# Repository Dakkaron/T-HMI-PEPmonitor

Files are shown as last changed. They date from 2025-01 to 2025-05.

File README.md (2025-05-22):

# PEPit Physiotherapy Game Console

(Für den Text in Deutsch bitte nach unten scrollen.)

## Disclaimer

PEPit is a toy. It uses a cheap commodity airpressure sensor to control games, which can help kids enjoy their physiotherapy more. It is not a medical product, it doesn't have research, papers or a big pharma company behind it. It does not give medical or physiotherapy advice and in no way does it replace an actual physician or physiotherapist. If you use PEPit you are aware that it is only a toy and not a medical product. If you use it you do so at your own risk and I will not be held liable for anything you do with your PEPit. You have been warned.

## Overview

Physiotherapy is challenging, especially for children with chronic conditions like Cystic Fibrosis. It takes time, is repetitive and often feels like a constant fight to get the child to actually do it right.

PepIt is a small handheld games console that connects to compatible physiotherapy devices (see list below). It automatically monitors the execution of physiotherapy tasks and rewards the player in game when the tasks are executed correctly.

It can also record every time it's used, so that your doctor or physiotherapist can review the data later.

This targets ages 5-10 due to the simplicity of the games so far, though anyone can use it.

PepIt is currently in early access, more games and features will follow.

## Compatible physiotherapy devices

- **Pari PEP S** with [Manometer Adapter](https://www.pari.com/int/products/pari-pep-systems/) (or similar devices)
- **Cegla RC-Cornet** and **RC-Cornet Plus** with [Pressure Measurement Adapter](https://cegla.de/files/downloads/manuals/RC-Druck-Mess-Adapter-manual-de.pdf)
- **Pari Boy** with **[LC Sprint Nebuliser](https://www.pari.com/int/products/inhalation-devices-for-the-lungs/pari-boy-classic-int/)**, using the Pari PEP S Manometer Adapter
- **[Pari E-Flow rapid](https://www.pari.com/int/products/inhalation-devices-for-the-lungs/eflow-rapid-nebuliser-system/)**, using the Pari PEP S Manometer Adapter
- Other inhalers or PEP devices that can fit the Pari PEP S or RC-Cornet manometer adapters
- Other inhalers or PEP devices that have manometer adapters
- Trampolines, using the Trampoline Sensor Addon (coming soon)

## Key Features

- **Make therapy fun**: Games with long-term motivation make the therapy engaging.
- **Reduce trouble**: No need to tell your kid that the task should be done better. PepIt automatically takes care of this.
- **Super easy to use**: PepIt is a standalone device. No booting a PC, trouble with glitchy Bluetooth connections or anything. Simply turn it on and use it.
- **Log therapy executions**: PepIt can optionally log all physiotherapy sessions so that your physiotherapists or doctors can review them later.
- **Configurable therapy routines**: Easily adjust PepIt to follow exactly the therapy routine your physiotherapist or doctor prescribed.
- **LUA-based, extendable game system**: Download additional games to the SD card later on. Or even create your own!

# PepIt Physiotherapie-Spielekonsole (Deutsch)

## Disclaimer

PEPit ist ein Spielzeug. Es verwendet billige, leicht verfügbare Luftdrucksensoren um Spiele zu steuern. Das kann dabei helfen, dass Kinder mehr Spaß an ihrer Physiotherapie haben. PEPit ist kein Medizinprodukt. Es hat weder Forschung, wissenschaftliche Arbeit oder einen Pharma-Konzern hinter sich. Es gibt keine Ratschläge im Bezug auf Medizin oder Physiotherapie und ersetzt auf keine Weise einen Arzt oder Physiotherapeuten. Wenn Sie PEPit verwenden, dann sind Sie sich hiermit bewusst, dass es ein Spielzeug und kein Medizinprodukt ist. Sie verwenden PEPit auf eigene Gefahr und eigenes Risiko hin und ich übernehme keine Haftung für was auch immer sie damit tun.

## Überblick

Seien wir mal ehrlich, Physiotherapie ist anstrengend, insbesondere für Kinder mit chronischen Krankheiten wie Zystische Fibrose/Mukoviszidose. Die Therapie frisst Zeit, ist monoton und es ist ein dauerhafter Kampf, das Kind dazu zu bringen, sie richtig auszuführen.

PepIt ist eine kleine tragbare Spielkonsole, die man mit kompatiblen Physiotherapiegeräten (siehe nachfolgende Liste) verbinden kann. Es erkennt automatisch die Ausführung der Physiotherapie und belohnt die Spielerin/den Spieler, wenn die Therapie korrekt ausgeführt wurde.

Optional können Nutzungsstatistiken von PepIt automatisch auf der SD-Karte gespeichert werden, sodass das medizinische Personal die Häufigkeit und Qualität der Therapieausführungen später auswerten kann.

PepIt zielt auf Kinder im Alter von 5 bis 10 Jahren ab, kann allerdings von Leuten aller Altersgruppen verwendet werden.

Aktuell befindet sich PepIt noch im Early Access. Weitere Spiele und Features werden im Laufe der Zeit folgen.

## Kompatible Physiotherapiegeräte

- **Pari PEP S** mit dem [Druckanzeiger-Adapter](https://www.pari.com/de/produkte/pari-pep-systeme/) (oder ähnliche Geräte)
- **Cegla RC-Cornet** und **RC-Cornet Plus** mit [Druck-Mess-Adapter](https://cegla.de/files/downloads/manuals/RC-Druck-Mess-Adapter-manual-de.pdf)
- **Pari Boy** mit **[LC Sprint Nebuliser](https://www.pari.com/int/products/inhalation-devices-for-the-lungs/pari-boy-classic-int/)**, unter Verwendung des Pari PEP S Druckanzeiger-Adapters
- **[Pari E-Flow rapid](https://www.pari.com/int/products/inhalation-devices-for-the-lungs/eflow-rapid-nebuliser-system/)**, unter Verwendung des Pari PEP S Druckanzeiger-Adapters
- Andere Inhalations- oder PEP-Geräte, auf die mit dem Pari PEP S Druckanzeiger-Adapter oder dem RC-Cornet-Druck-Mess-Adapter kompatibel sind
- Andere Inhalations- oder PEP-Geräte mit Manometeranschluss oder Druckmess-Adapter
- Trampoline unter Verwendung des Trampolin-Sensor-Addons (kommt demnächst)

## Wichtigste Features

- **Interessantere Therapie**: Spiele mit Langzeitmotivation machen die Therapie interessanter.
- **Weniger Ärger**: Mit PepIt müssen Sie nicht mehr mit dem Kind darüber streiten, ob es die Therapie korrekt ausführt. PepIt übernimmt das automatisch.
- **Sehr einfach zu verwenden**: PepIt ist Standalone. Man braucht dafür keinen PC booten, kein Handy per Bluetooth koppeln oder sonst etwas. Einfach einschalten und es nutzen.
- **Therapie loggen**: Optional kann PepIt die Nutzung auf die SD-Karte loggen, sodass das zuständige medizinische Personal sie im Nachhinein auswerten kann.
- **Anpassbare Therapiepläne**: Die Therapiepläne können in PepIt leicht auf die Anordnung der Physiotherapeuten oder Ärzte angepasst werden.
- **LUA-basiertes, erweitertes Spielsystem**: Zusätzliche Spiele können nachträglich auf die SD-Karte gespielt werden. Es ist sogar möglich, selbst welche zu erstellen!

## Bauanleitung
[Hier klicken um zur Bauanleitung zu kommen.](docs/Parts_de.md)

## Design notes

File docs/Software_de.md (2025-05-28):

# SD-Karte vorbereiten

1. Die SD-Karte mit einem Computer verbinden. Dafür kann entweder ein integrierter SD-Karten-Slot im PC oder ein SD-Karten-Adapter verwendet werden.
2. Die Datei sdcardcontent.zip vom neuesten [Release](https://github.com/Dakkaron/T-HMI-PEPmonitor/releases) herunterladen und den Inhalt auf die SD-Karte entpacken.

# Firmware auf LILLYGO T-HMI aufspielen

1. Das neueste firmware.bin von der [Release-Seite](https://github.com/Dakkaron/T-HMI-PEPmonitor/releases) herunterladen.
1. LILLYGO T-HMI per USB-Kabel mit dem PC verbinden. Sollte das Display des LILLYGO T-HMI nicht angehen, sobald es mit dem PC verbunden ist, bitte ein USB-A-auf-USB-C-Kabel verwenden. Bei der Verwendung von USB-C-auf-USB-C-Kabeln kann es zu Problemen kommen.
2. [flash_download_tool](https://dl.espressif.com/public/flash_download_tool.zip) herunterladen und ausführen.
3. Im flash_download_tool `ChipType:` auf `ESP32-S3` stellen:
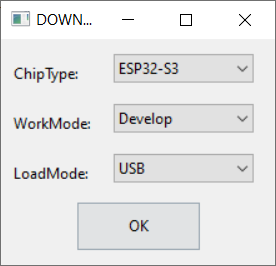
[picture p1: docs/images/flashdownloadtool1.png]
flash_download_tool
 und mit `OK` bestätigen.
4. Auf der zweiten Seite folgende Einstellungen auswählen:
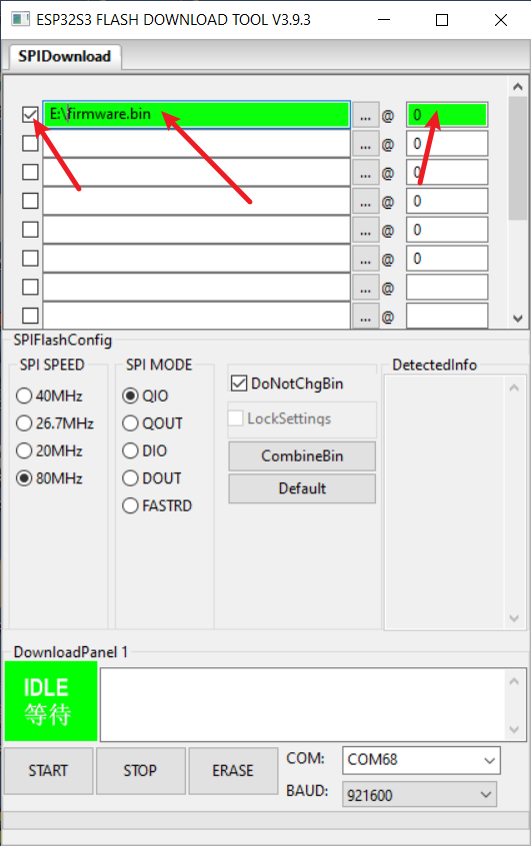
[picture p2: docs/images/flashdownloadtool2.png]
flash_download_tool

   * Oberste Checkbox am linken Rand aktivieren
   * Im Textfeld rechts neben der Checkbox den Pfad zu `firmware.bin` angeben
   * Sicherstellen, dass im rechtesten Textfeld der Zeile eine 0 ist.
   * Rechts unten bei `BAUD:` 921600 eingeben.
   * Bestätigen mit einem Click auf `START`
5. Wenn das Hochladen abgeschlossen ist, kann der T-HMI vom PC getrennt werden.

# Testen

1. MicroSD-Karte in den Slot im T-HMI einschieben.
2. Das T-HMI per USB mit dem PC verbinden.
3. Das T-HMI sollte beim ersten Start die Touchscreen-Kalibrierung anzeigen, danach wird das Hauptmenü angezeigt.

Nächster Schritt: [Zusammenbau](Assembly_de.md)

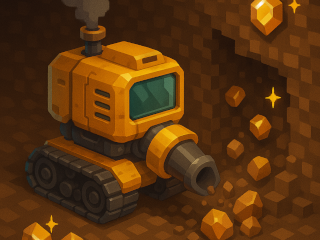
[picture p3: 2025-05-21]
SDCardContent/games/miner/gfx/win/win1.bmp

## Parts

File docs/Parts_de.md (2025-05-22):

# Benötigte Werkzeuge

- Schraubenzieher
- Lötkolben mit Lötzinn
- Werkzeug zum Abisolieren von Kabeln
- 3D-Drucker (optional)
- PC mit Windows (Andere Betriebssysteme sind möglich, werden aber in diesem Guide aktuell nicht behandelt)
- SD-Karte zu USB Adapter (falls man im PC keinen SD-Karten-Slot hat)
- Patafix oder doppelseitiges Klebeband

# Benötigte Bauteile

## Elektronische Bauteile

- LILLYGO T-HMI: https://lilygo.cc/products/t-hmi
- Luftdrucksensor: https://de.aliexpress.com/item/1005006421627550.html

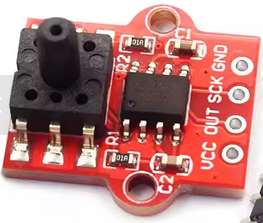
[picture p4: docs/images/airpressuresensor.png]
Luftdrucksensor

- 1S Akku mit PH2.0 Anschluss, mindestens 200mA (https://de.aliexpress.com/item/1005007256417369.html)
- MicroSD-Karte mit mindestens 1GB und maximal 32GB.

## Schrauben

- 4x M3x25 Schrauben
- 4x M3 Muttern, viereckig
- 4x M2x10 Schrauben

## Sonstiges

- Doppelseitiges Klebeband, am Besten Tesa Powerstrips Small

## 3D-Druck

- Obere Hälfte: (https://github.com/Dakkaron/T-HMI-PEPmonitor/blob/main/3DPrint/T_HMI_PEP_case_v3.2_top.stl)
- Untere Hälfte: (https://github.com/Dakkaron/T-HMI-PEPmonitor/blob/main/3DPrint/T_HMI_PEP_case_v3.2_bottom_with_tpu.stl)
- Schlauch-Adapter: (https://github.com/Dakkaron/T-HMI-PEPmonitor/blob/main/3DPrint/PEP_adapter.stl)

Der Schlauchadapter muss mit flexiblem Material (z.B. TPU- oder TPE-Filament) gedruckt werden.

Sollte kein 3D-Drucker zur Verfügung stehen, bietet sich der Druckservice von [JLC3DP](https://jlc3dp.com) an.

### Anleitung für JLC3DP

1. LadenSie die drei STL Dateien aus dem letzten Punkt herunter.
2. Öffnen sie [https://jlc3dp.com](https://jlc3dp.com) in ihrem Browser.
3. Klicken sie auf "Order Now"
4. Klicken sie auf "Add 3D Files" und fügen sie alle drei STL-Dateien nacheinander hinzu.
5. Für die beiden Gehäuseteile wählen sie einen passenden Druckprozess und Material aus. `FDM(Plastic)` -> `PLA` funktioniert gut, aber andere Materialien sollten auch verwendbar sein.
6. Für den PEP_adapter.stl wählen sie `FDM(Plastic)` -> `TPU`
7. Farben können beliebig gewählt werden.
8. Drücken Sie "Save to cart" und folgen Sie dem Bestellprozess.
9. `Global Direct Line`-Versand ist mit Abstand der Billigste, dauert dafür normal 1-2 Wochen.

Nächster Schritt: [Software installieren](Software_de.md)

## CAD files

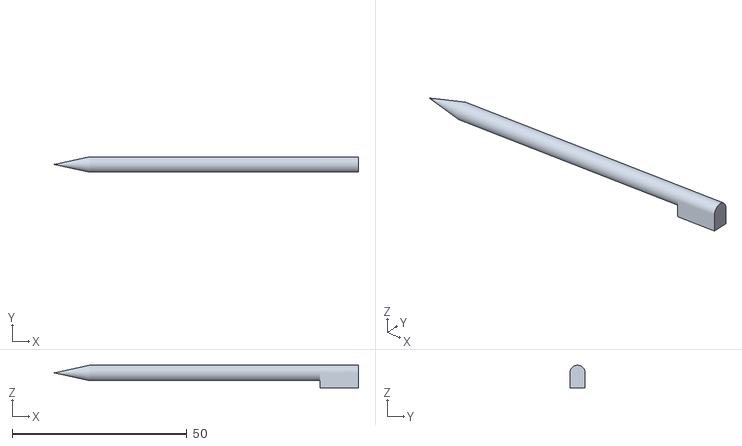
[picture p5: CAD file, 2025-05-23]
3DPrint/Stylus.stl
87.0 x 4.42 x 6.47

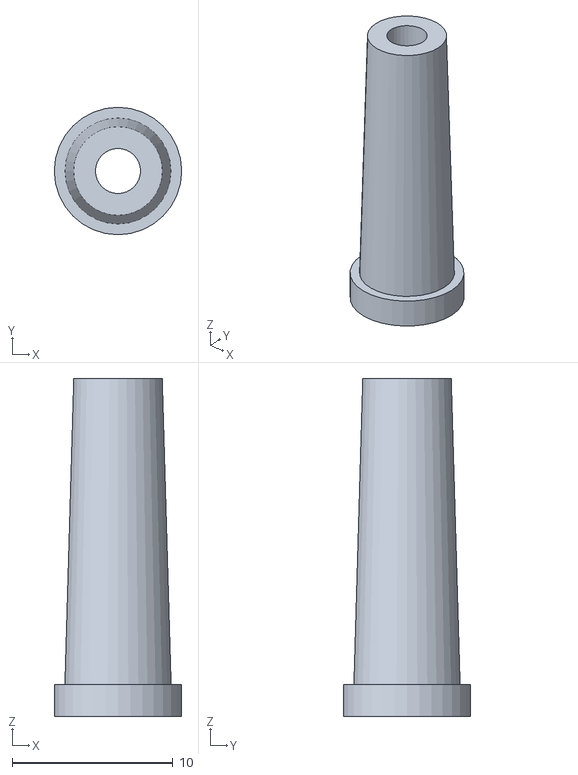
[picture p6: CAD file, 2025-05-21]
3DPrint/PEP_adapter.stl
7.92 x 7.92 x 21.0

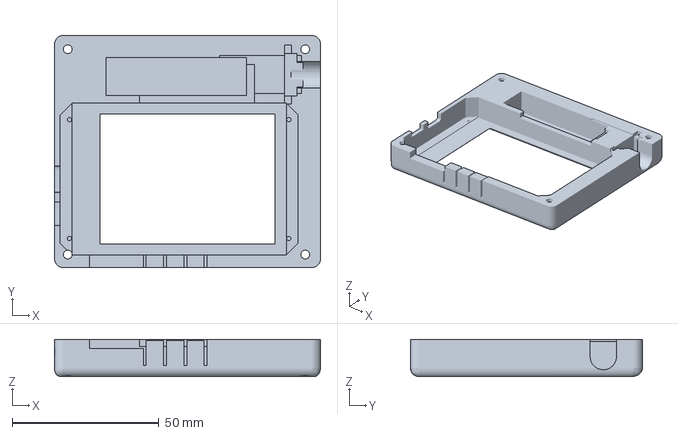
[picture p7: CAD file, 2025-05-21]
3DPrint/T_HMI_PEP_case_v3.3_top_with_logo.3mf
90.7 x 79.2 x 12.8 mm

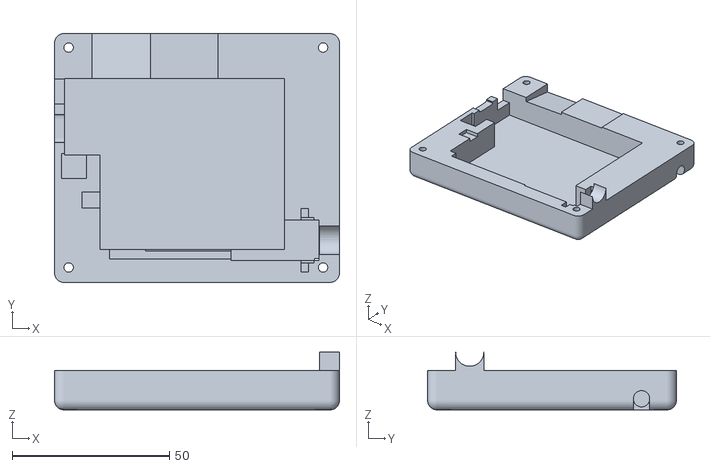
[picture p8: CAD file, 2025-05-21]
3DPrint/T_HMI_PEP_case_v3.3_bottom.stl
90.7 x 79.2 x 18.4

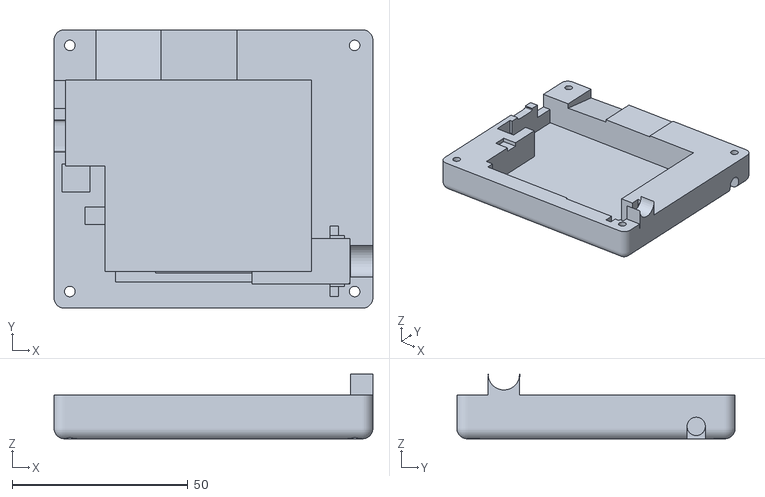
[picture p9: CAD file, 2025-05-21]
3DPrint/T_HMI_PEP_case_v3.3_bottom_hexnuts.stl
90.7 x 79.2 x 18.4

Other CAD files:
3DPrint/T_HMI_PEP_case_v3.3_top.stl

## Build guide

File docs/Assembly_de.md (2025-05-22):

# Löten

- Das bei dem T-HMI mitgelieferte Grove-Kabel (das Kabel mit den vier Adern) in der Mitte durchschneiden und die Adern rund 5mm tief abisolieren.
- Die vier Adern in der folgenden Reihenfolge an den Luftdrucksensor anlöten:
   - Schwarz -> GND
   - Rot -> VCC
   - Gelb -> OUT
   - Weiß -> SCK

# Verkablen

- Den Grove-Connector vom letzten Schritt in den mittleren Grove-Steckplatz am T-HMI anschließen.
- Den Akku an den `BAT`-Steckplatz am T-HMI anschließen

# Verschrauben

- Das T-HMI in den oberen Teil des Gehäuses einsetzen und mit den vier M2x10-Schrauben verschrauben.
- Die vier Muttern in die Aussparungen des unteren Gehäuses eindrücken.
- Die Batterie mittels Patafix oder doppelseitigem Klebeband (z.B. Tesa Power Strips Small) in die untere Gehäusehälfte kleben.
- Den Luftdrucksensor in die passende Aussparung in der oberen Gehäusehälfte einsetzen.
- Die obere Gehäusehälfte auf die Untere aufsetzen.
- Die vier M3-Schrauben in die Ecken der oberen Gehäusehälfte einsetzen und festschrauben.

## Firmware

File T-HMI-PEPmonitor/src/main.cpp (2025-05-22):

#include <Arduino.h>
#define CONFIG_SPIRAM_SUPPORT 1

#include "systemconfig.h"
#include "constants.h"

#include <SD_MMC.h>
#include <FS.h>
#include <SPI.h>
#include <SD.h>
#include <OneButton.h>

#include "hardware/gfxHandler.hpp"
#include "hardware/pressuresensor.h"
#include "hardware/touchHandler.h"
#include "hardware/wifiHandler.h"
#include "hardware/sdHandler.h"
#include "games/games.h"
#include "hardware/serialHandler.h"
#include "hardware/powerHandler.h"
#include "physioProtocolHandler.h"
#include "updateHandler.h"

void setBrightness(uint8_t value) {
  static uint8_t _brightness = 0;

  if (_brightness == value) {
    return;
  }
  value = _min(16, value);
  if (value == 0) {
    digitalWrite(BK_LIGHT_PIN, 0);
    delay(3);
    _brightness = 0;
    return;
  }
  if (_brightness == 0) {
    digitalWrite(BK_LIGHT_PIN, 1);
    _brightness = SCREEN_BRIGHTNESS_STEPS;
    delayMicroseconds(30);
  }
  int from = SCREEN_BRIGHTNESS_STEPS - _brightness;
  int to = SCREEN_BRIGHTNESS_STEPS - value;
  int num = (SCREEN_BRIGHTNESS_STEPS + to - from) % SCREEN_BRIGHTNESS_STEPS;
  for (int i = 0; i < num; i++) {
    digitalWrite(BK_LIGHT_PIN, 0);
    digitalWrite(BK_LIGHT_PIN, 1);
  }
  _brightness = value;
}

void setup() {
  pinMode(PWR_ON_PIN, OUTPUT);
  digitalWrite(PWR_ON_PIN, HIGH);
  pinMode(BK_LIGHT_PIN, OUTPUT);
  digitalWrite(BK_LIGHT_PIN, HIGH);

  esp_log_level_set("gpio", ESP_LOG_ERROR);

  Serial.setRxBufferSize(10240);
  Serial.setTxBufferSize(1024);
  Serial.begin(115200);

  pinMode(PWR_EN_PIN, OUTPUT);
  digitalWrite(PWR_EN_PIN, HIGH);

  tft.init();
  tft.setRotation(SCREEN_ROTATION);
  tft.setSwapBytes(true);
  tft.fillScreen(TFT_BLACK);

  setBrightness(16);

  initGfxHandler();
  tft.setTextSize(2);
  tft.drawString("Nicht", 10, 10);
  tft.drawString("blasen!", 10, 25);
  initPressureSensor();

  initTouch();

  buttonPwr.attachClick(power_off);
  buttonPwr.attachLongPressStop(power_off);
  buttonUsr.attachLongPressStop(runTouchCalibration);

  randomSeed(analogRead(0));
  
  String errorMessage;
  initSD(&errorMessage);
  checkFailWithMessage(errorMessage);
  checkForPrefsReset();
  initSystemConfig(&errorMessage);
  checkFailWithMessage(errorMessage);

  drawBmp("/gfx/splash.bmp", 0, 0);
  uint8_t defaultTextDatum = tft.getTextDatum();
  tft.setTextColor(TFT_BLACK);
  tft.setTextDatum(TR_DATUM);
  tft.drawString("Version "+String(VERSION), 320, 2);
  tft.setTextDatum(defaultTextDatum);
  delay(1000);
  Serial.print("PEPit Version '");
  Serial.print(VERSION);
  Serial.println("'");
  Serial.print("Initializing peripherals....");
  delay(1000);

  Serial.println(F("done"));
  
  Serial.print("PEPit Version '");
  Serial.print(VERSION);
  Serial.println("' initialized");

  tft.setTextSize(1);
  tft.drawString("Warte auf WLAN-Verbindung...", 0, 230);

  uint32_t requiredTaskTypes = runProfileSelection();
  runGameSelection(requiredTaskTypes);
  displayPhysioRotateScreen();
}

void loop() {
  buttonPwr.tick();
  buttonUsr.tick();
  handleSerial();
  handlePhysioTask();
  /*Serial.print("Free heap: ");
  Serial.println(ESP.getFreeHeap());*/
}

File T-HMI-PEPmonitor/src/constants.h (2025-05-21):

#ifndef __CONSTANTS_H__
#define __CONSTANTS_H__
#include <Arduino.h>

#define VERSION "1.1"

#define LAST_BLOW_SUCCEEDED 0B00000001
#define LAST_BLOW_FAILED    0B00000010
#define NEW_BLOW            0B00000100

#define PRESSURE_BAR_WIDTH 180
#define PRESSURE_BAR_HEIGHT 10
#define PRESSURE_BAR_X 1
#define PRESSURE_BAR_Y 190

#define PRESSURE_SENSOR_DIVISOR 65L
#define PRESSURE_SENSOR_CUTOFF_LIMIT 500
#define PRESSURE_SENSOR_SMOOTHING_NUM_READINGS 10
#define PRESSURE_SENSOR_MAX_SKIPS 10;

#define PRESSURE_SENSOR_CUMULATIVE_ERROR_FACTOR 16

#define SCREEN_BRIGHTNESS_STEPS 16
#define SCREEN_ROTATION 3
#define SCREEN_WIDTH 320
#define SCREEN_HEIGHT 240

#define HX7711_DATA_PIN 17
#define HX7711_CLOCK_PIN 18

#define SIMULATE_BLOWS_SHORT_BLOW_DURATION 1000
#define SIMULATE_BLOWS_PAUSE_DURATION 5000

#define BATTERY_LOW_WARNING_VOLTAGE 3400
#define BATTERY_LOW_SHUTDOWN_VOLTAGE 3300

#define SENSOR_MODE_PEPS 1
#define SENSOR_MODE_TRAMPOLINE 2

#define PROGRESS_MENU_SELECTION_ID 32767
#define SYSTEM_UPDATE_SELECTION_ID 32766
#define EXECUTION_LIST_SELECTION_ID 32765

#define PROFILE_TASK_TYPE_SHORTBLOWS 1
#define PROFILE_TASK_TYPE_LONGBLOWS 2
#define PROFILE_TASK_TYPE_EQUALBLOWS 3
#define PROFILE_TASK_TYPE_TRAMPOLINE 4
#define PROFILE_TASK_TYPE_INHALATION 5

#define INHALATION_TASK_WARN_TIMEOUT 10000L
#define INHALATION_TASK_END_TIMEOUT 15000L

#define MAX_WIFI_NETWORKS 3
#define FILE_DOWNLOAD_CHUNK_SIZE 1024*10
#define FILE_DOWNLOAD_TO_STRING_MAX_SIZE 1024
#define FIRMWARE_RELEASE_PATH_URL "https://raw.githubusercontent.com/Dakkaron/T-HMI-PEPmonitor/refs/heads/main/path_to_latest_release"
#define LAST_RELEASE_URL_FILE_PATH "/lastReleaseUrl.txt"
#define FIRMWARE_FILE_NAME "firmware.bin"
#define SDCARD_CONTENT_FILE_NAME "SDCardContent.tar"

#define GAME_SELECTION_POWEROFF_TIMEOUT 3L*60L*1000L // Power off device if it spends >3 minutes on game selection screen
#define WIN_SCREEN_TIMEOUT 3L*60L*1000L

#define REQUIRED_TASK_TYPE_SHORTBLOWS       0b00000001
#define REQUIRED_TASK_TYPE_LONGBLOWS        0b00000010
#define REQUIRED_TASK_TYPE_EQUALBLOWS       0b00000100
#define REQUIRED_TASK_TYPE_TRAMPOLINE       0b00001000
#define REQUIRED_TASK_TYPE_INHALATION       0b00010000
#define REQUIRED_TASK_TYPE_PROGRESSION_MENU 0b00100000

struct GameConfig {
  String name;
  String templateName;
  String prefsNamespace;
};

struct ProfileData {
  String name;
  String imagePath;
  uint8_t cycles;
  uint8_t tasks;
  uint8_t taskType[10];
  uint8_t taskRepetitions[10];
  String taskChangeImagePath[10];
  String taskChangeMessage[10];
  uint32_t taskTime[10];
  uint32_t taskMinStrength[10];
  bool taskNegativeStrength[10];
  uint32_t taskTargetStrength[10];
};


struct BlowData {
  bool currentlyBlowing = false;
  unsigned long ms = 0;
  unsigned long blowStartMs = 0;
  unsigned long blowEndMs = 0;
  unsigned long targetDurationMs = 0;
  unsigned long totalTimeSpentBreathing = 0;
  unsigned long taskStartMs;
  int32_t breathingScore = 0;
  uint8_t cycleNumber = 0;
  uint8_t totalCycleNumber = 0;
  uint8_t taskNumber = 0;
  uint8_t totalTaskNumber = 0;
  uint8_t blowCount = 0;
  uint8_t totalBlowCount = 0;
  int32_t pressure = 0;
  bool negativePressure = false;
  int32_t peakPressure = 0;
  int32_t minPressure = 0;
  int32_t targetPressure = 0;
  uint32_t cumulativeError = 0;
  uint8_t fails = 0;
  uint32_t taskType;
  uint8_t lastBlowStatus = 0;
  uint32_t totalLongBlowRepetitions = 0;
  uint32_t totalEqualBlowRepetitions = 0;
  uint32_t totalShortBlowRepetitions = 0;
};


struct JumpData {
  unsigned long ms;
  uint8_t cycleNumber = 0;
  uint8_t totalCycleNumber = 0;
  uint8_t taskNumber = 0;
  uint8_t totalTaskNumber = 0;
  uint16_t jumpCount = 0;
  bool currentlyJumping = false;
  int32_t msLeft = 0;
  int32_t totalTime = 0;
  uint16_t misses = 0;
  uint16_t highscore = 0;
  bool newHighscore = false;
  bool lastReadSuccessful = false;
};

#endif /* __CONSTANTS_H__ */

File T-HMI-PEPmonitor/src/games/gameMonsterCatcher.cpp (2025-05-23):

#include "gameMonsterCatcher.h"

static String monsterCatcherGamePath;
static String monsterCatcherGameIniPath;
static uint16_t maxMonsterCount;
static uint16_t monsterCount;

static TFT_eSprite playerSprite[] = {TFT_eSprite(&tft), TFT_eSprite(&tft), TFT_eSprite(&tft), TFT_eSprite(&tft)};
static TFT_eSprite enemySprite[] = {TFT_eSprite(&tft), TFT_eSprite(&tft)};
static TFT_eSprite safariBushSprite[] {TFT_eSprite(&tft), TFT_eSprite(&tft), TFT_eSprite(&tft), TFT_eSprite(&tft)};
static TFT_eSprite ballCaughtIndicator = TFT_eSprite(&tft);
static MonsterData playerMonsterData;
static MonsterData enemyMonsterData;
static uint8_t* monsterLevels;
static String loadedAttacks[2] = {"",""}; //-1 == no attack loaded
static TFT_eSprite* attackSprites[2] = {nullptr, nullptr};

static void loadPlayerMonsterId(String* errorMessage);
static void savePlayerMonsterId();


static uint16_t getRandomPreviouslyCaughtMonster() {
  uint16_t monsterId = 0;
  while (true) {
    monsterId = random(0, monsterCount);
    if (monsterLevels[monsterId] > 0) {
      return monsterId;
    }
    vTaskDelay(1); // watchdog
  }
}

static uint16_t countMonstersCaught() {
  uint16_t caughtMonsters = 0;
  for (uint32_t i = 0; i<monsterCount; i++) {
    if (monsterLevels[i] > 0) {
      caughtMonsters++;
    }
  }
  return caughtMonsters;
}

static uint8_t attackDodgeBoilerplate(BlowData* blowData, bool playerIsAttacking) {
    if (blowData->lastBlowStatus == LAST_BLOW_FAILED) {
      if (playerIsAttacking) {
        return DRAW_PLAYER_ALIVE | DRAW_ENEMY_DODGE;
      } else {
        return DRAW_PLAYER_ALIVE | DRAW_ENEMY_ALIVE;
      }
    } else {
      if (playerIsAttacking) {
        return DRAW_PLAYER_ALIVE | DRAW_ENEMY_ALIVE;
      } else {
        return DRAW_PLAYER_DODGE | DRAW_ENEMY_ALIVE;
      }
    }
}

uint8_t attackFunction_confusion(DISPLAY_T* display, BlowData* blowData, bool playerIsAttacking, int32_t animTime, bool draw) {
  if (!draw) {
    return attackDodgeBoilerplate(blowData, playerIsAttacking);
  }
  if (animTime >= 2000 || blowData->lastBlowStatus == NEW_BLOW) {
    return DRAW_PLAYER_ALIVE | DRAW_ENEMY_ALIVE;
  }
  if (animTime<1900) {
    tft.invertDisplay(!((animTime / 250) % 2));
  } else {
    tft.invertDisplay(0);
  }
  return 0;
}

uint8_t attackFunction_catch(DISPLAY_T* display, BlowData* blowData, bool playerIsAttacking, int32_t animTime, bool draw) {
  if (!draw) {
    if (blowData->lastBlowStatus == LAST_BLOW_FAILED) {
      return DRAW_PLAYER_ALIVE | DRAW_ENEMY_DODGE;
    } else if (animTime >= 2000 || blowData->lastBlowStatus == NEW_BLOW) {
      return DRAW_PLAYER_ALIVE | DRAW_ENEMY_ALIVE;
    } else {
      return DRAW_PLAYER_ALIVE;
    }
  }
  if (animTime >= 2000 || blowData->lastBlowStatus == NEW_BLOW) {
    return DRAW_PLAYER_ALIVE | DRAW_ENEMY_ALIVE;
  }
  if (animTime<500) {
    int16_t animOffset = (500-animTime) / 4;
    attackSprites[0][0].pushToSprite(display, 200+16-animOffset, 50-32+(animOffset/3), 0x0000);
  } else if (animTime<1000) {
    attackSprites[0][1].pushToSprite(display, 200+16, 50+32, 0x0000);
  } else if (animTime<1500) {
    int16_t animOffset = (1500-animTime) / 8;
    attackSprites[0][0].pushToSprite(display, 200+11+((animTime/250)% 3)*5, 50+32-animOffset, 0x0000);
  } else {
    attackSprites[0][0].pushToSprite(display, 200+11+((animTime/250)% 3)*5, 50+32, 0x0000);
  }
  return 0;
}

uint8_t attackFunction_rareCandy(DISPLAY_T* display, BlowData* blowData, bool playerIsAttacking, int32_t animTime, bool draw) {
  if (!draw) {
    if (blowData->lastBlowStatus == LAST_BLOW_FAILED) {
      return DRAW_PLAYER_ALIVE | DRAW_ENEMY_DODGE;
    } else if (animTime >= 2000 || blowData->lastBlowStatus == NEW_BLOW) {
      return DRAW_PLAYER_ALIVE | DRAW_ENEMY_ALIVE;
    } else {
      return DRAW_PLAYER_ALIVE | DRAW_ENEMY_ALIVE;
    }
  }
  if (animTime >= 2000 || blowData->lastBlowStatus == NEW_BLOW) {
    return DRAW_PLAYER_ALIVE | DRAW_ENEMY_ALIVE;
  }
  if (animTime<1000) {
    int16_t animOffset = (1000-animTime) / 7;
    attackSprites[0][0].pushToSprite(display, 200+16-animOffset, 50+32+(animOffset/3), 0x0000);
  } else {
    attackSprites[0][0].pushToSprite(display, 200+11+((animTime/250)% 3)*5, 50+32, 0x0000);
  }
  return 0;
}

uint8_t attackFunction_ember(DISPLAY_T* display, BlowData* blowData, bool playerIsAttacking, int32_t animTime, bool draw) {
  if (!draw) {
    return attackDodgeBoilerplate(blowData, playerIsAttacking);
  }
  if (animTime >= 2000 || blowData->lastBlowStatus == NEW_BLOW) {
    return DRAW_PLAYER_ALIVE | DRAW_ENEMY_ALIVE;
  }
  uint8_t animCount = _max(1, playerIsAttacking ? playerMonsterData.attack.animFrames : enemyMonsterData.attack.animFrames);
  uint16_t msPerAnimFrame = _max(1, 2000 / animCount);
  uint8_t animFrame = animCount - 1 - _min(animCount - 1, animTime / msPerAnimFrame);
  if (playerIsAttacking) {
    if (animTime<1000) {
      int16_t animOffset = (1000-animTime) / 7;
      attackSprites[!playerIsAttacking][animFrame].pushToSprite(display, 200+16-animOffset, 50+32+(animOffset/3), 0x0000);
    } else {
      attackSprites[!playerIsAttacking][animFrame].pushToSprite(display, 200+6+((animTime/250)% 3)*10, 50+32, 0x0000);
    }
  } else {
    if (animTime<1000) {
      int16_t animOffset = (1000-animTime) / 7;
      attackSprites[!playerIsAttacking][animFrame].pushToSprite(display, 50+16+animOffset, 100+32-(animOffset/3), 0x0000);
    } else {
      attackSprites[!playerIsAttacking][animFrame].pushToSprite(display, 50 + 6 + ((animTime / 250) % 3) * 10, 100+32, 0x0000);
    }
  }
  return 0; // On draw==true, the return value is ignored;
}

uint8_t attackFunction_throwFastAnim(DISPLAY_T* display, BlowData* blowData, bool playerIsAttacking, int32_t animTime, bool draw) {
  if (!draw) {
    return attackDodgeBoilerplate(blowData, playerIsAttacking);
  }
  if (animTime >= 2000 || blowData->lastBlowStatus == NEW_BLOW) {
    return DRAW_PLAYER_ALIVE | DRAW_ENEMY_ALIVE;
  }
  uint8_t animCount = _max(1, playerIsAttacking ? playerMonsterData.attack.animFrames : enemyMonsterData.attack.animFrames);
  uint8_t animFrame = (animTime / 100) % animCount;
  if (playerIsAttacking) {
    if (animTime<1000) {
      int16_t animOffset = (1000-animTime) / 7;
      attackSprites[!playerIsAttacking][animFrame].pushToSprite(display, 200+16-animOffset, 50+32+(animOffset/3), 0x0000);
    } else {
      attackSprites[!playerIsAttacking][animFrame].pushToSprite(display, 200+6+((animTime/250)% 3)*10, 50+32, 0x0000);
    }
  } else {
    if (animTime<1000) {
      int16_t animOffset = (1000-animTime) / 7;
      attackSprites[!playerIsAttacking][animFrame].pushToSprite(display, 50+16+animOffset, 100+32-(animOffset/3), 0x0000);
    } else {
      attackSprites[!playerIsAttacking][animFrame].pushToSprite(display, 50 + 6 + ((animTime / 250) % 3) * 10, 100+32, 0x0000);
    }
  }
  return 0; // On draw==true, the return value is ignored;
}

uint8_t attackFunction_scratch(DISPLAY_T* display, BlowData* blowData, bool playerIsAttacking, int32_t animTime, bool draw) {
  if (!draw) {
    return attackDodgeBoilerplate(blowData, playerIsAttacking);
  }
  if (animTime >= 2000 || blowData->lastBlowStatus == NEW_BLOW) {
    return DRAW_PLAYER_ALIVE | DRAW_ENEMY_ALIVE;
  }
  uint8_t animCount = _max(1, playerIsAttacking ? playerMonsterData.attack.animFrames : enemyMonsterData.attack.animFrames);
  uint8_t animFrame = (animTime / 100) % animCount;
  if (playerIsAttacking) {
    attackSprites[!playerIsAttacking][animFrame].pushToSprite(display, 200+6+((animTime/250)% 3)*10, 50+32, 0x0000);
  } else {
    attackSprites[!playerIsAttacking][animFrame].pushToSprite(display, 50 + 6 + ((animTime / 250) % 3) * 10, 100+32, 0x0000);
  }
  return 0; // On draw==true, the return value is ignored;
}
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

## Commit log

2024-09-25 Added trampoline sensor support, trampoline safari zone game, refactoring
2024-09-25 Move from Arduino IDE to Platformio
2024-10-23 Performance improvements for pressure sensor
2024-11-14 Fixing IRQ pin mode for touch
2024-11-16 Added battery icon, improved FPS counter
2024-12-05 Improved PEP hole swap screen
2024-12-06 Reduced shutoff voltage limits
2024-12-19 3D print files
    [T_HMI_PEP_case_v3.2.blend, T_HMI_PEP_case_v3.2_bottom_with_tpu.stl, T_HMI_PEP_case_v3.2_top.stl]
2024-12-20 Display power status on win screen and game selection screen;auto power off on win screen after a few minutes
2024-12-26 settings and board
2024-12-26 Added poweroff charge-only screen
2024-12-26 Powerbutton handling on game selection screen
2024-12-28 #16, #17 physio protocol configuration from SD; touchscreen calibration
2024-12-29 Small improvements to touch calibration and low battery display
2024-12-29 Low battery warning improvement
2024-12-29 Added negative pressure handling for tasks in preparation to inhaler integration
2024-12-30 added PEP_adapter.stl
    [PEP_adapter.stl]
2025-01-01 Airpressure sensor image
2025-01-01 Adapted PEP_adapter.stl to work with JLC3DP
    [PEP_adapter.stl]
2025-01-01 Assembly guide german
2025-01-02 Pressure sensor refactoring
2025-01-03 Fixed pressure sensing issue
2025-02-11 Fixed battery voltage indicator bug
2025-05-13 Move from pure Arduino to Arduino as an ESP-IDF component
    [default_16MB.csv]
2025-05-17 miner game stages
2025-05-21 Updated 3D print files
    [PEP_adapter.stl, T_HMI_PEP_case_v3.2.blend, T_HMI_PEP_case_v3.2_bottom_with_tpu.stl, T_HMI_PEP_case_v3.2_top.stl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]
2025-05-23 Added stylus 3D print file
    [Stylus.stl]
